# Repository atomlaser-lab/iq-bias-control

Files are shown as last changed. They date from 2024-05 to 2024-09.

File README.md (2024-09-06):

# IQ Modulator Bias Control

This project implements a digital bias controller for an IQ modulator running in carrier-suppressed single-sideband (CS-SSB) mode.  It is based on [this paper](http://opg.optica.org/ao/abstract.cfm?uri=ao-62-1-1) which detailed an analog stabilisation scheme using the same technique.  Our arXiv submission, with more detail about our digital implementation and performance, can be found [here](https://arxiv.org/abs/2408.16678).  The basic idea is to add a low frequency signal to the main, high frequency signal used for CS-SSB and use the low frequency signal to measure the phase biases in the different Mach-Zehnder interferometers (MZIs) that make up the IQ modulator.  Whereas the original work used purely analog techniques, this project levarages the fast analog input/output capabilities of the Red Pitaya STEMlab 125-14 platform.  

# Software set up

  1. Clone both this repository and the interface repository at [https://github.com/atomlaser-lab/red-pitaya-interface](https://github.com/atomlaser-lab/red-pitaya-interface) to your computer.  

  2. Connect the Red Pitaya (RP) board to an appropriate USB power source (minimum 2 A current output), and then connect it to the local network using an ethernet cable.  Using SSH (via terminal on Linux/Mac or something like PuTTY on Windows), log into the RP using the hostname `rp-{MAC}.local` where `{MAC}` is the last 6 characters of the RP's MAC address which is written on the ethernet connector.  Your network may assign its own domain, so `.local` might not be the correct choice.  The default user name and password for RPs is `root`.  Once logged in, create two directories called `iq-bias-control` and `server`.

  3. From this repository, copy over all files in the 'software/programs/' directory to the `iq-bias-control` directory on the RP using either `scp` (from a terminal on your computer) or using your favourite GUI (I recommend WinSCP for Windows).  Also copy over the file `fpga/iq-bias-control.bit` to the `iq-bias-control` directory.  From the interface repository, copy over all files ending in '.py' and the file 'get_ip.sh' to the `server` directory on the RP.

  4. On the RP and in the `iq-bias-control` directory, compile the C programs.  You can compile these using the Makefile by running the command `make` with no arguments.  This will compile all the C programs in the directory.  

  5. In the `server` directory, change the privileges of `get_ip.sh` using `chmod a+x get_ip.sh`.  Check that running `./get_ip.sh` produces a single IP address (you may need to install dos2unix using `apt install dos2unix` and then run `dos2unix get_ip.sh` to make it work).  If it doesn't, run the command `ip addr` and look for an IP address that isn't `127.0.0.1` (which is the local loopback address).  There may be more than one IP address -- you're looking for one that has tags 'global' and 'dynamic'.  Here is the output from one such device:
   ```
   root@rp-f0919a:~# ip addr
   1: lo: <LOOPBACK,UP,LOWER_UP> mtu 65536 qdisc noqueue state UNKNOWN group default qlen 1
      link/loopback 00:00:00:00:00:00 brd 00:00:00:00:00:00
      inet 127.0.0.1/8 scope host lo
         valid_lft forever preferred_lft forever
      inet6 ::1/128 scope host 
         valid_lft forever preferred_lft forever
   2: eth0: <BROADCAST,MULTICAST,UP,LOWER_UP> mtu 1500 qdisc pfifo_fast state UP group default qlen 1000
      link/ether 00:26:32:f0:91:9a brd ff:ff:ff:ff:ff:ff
      inet 169.254.176.82/16 brd 169.254.255.255 scope link eth0
         valid_lft forever preferred_lft forever
      inet 192.168.1.109/24 brd 192.168.1.255 scope global dynamic eth0
         valid_lft 77723sec preferred_lft 77723sec
   3: sit0@NONE: <NOARP> mtu 1480 qdisc noop state DOWN group default qlen 1
      link/sit 0.0.0.0 brd 0.0.0.0
   ```
   The IP address we want here is the address `192.168.1.109` as it has the `global` tag, which is what `get_ip.sh` looks for.  If you have your RP connected directly to your computer it will not work and you will have to specify the IP address manually.

   6. Upload the bitstream to the FPGA by navigating to the `iq-bias-control` directory and running `cat iq-bias-control.bit > /dev/xdevcfg`.

   7. Start the Python server by navigating to the `iq-bias-control` directory and running `python3 /root/server/appserver.py`.  If you need to specify your IP address run instead `python3 /root/server/appserver.py <ip address>`.  The script will print the IP address it is using on the command line, saying `Listening on <IP address>`.

   8. On your computer in MATLAB, add the interface repository directory to your MATLAB path.

   9. Navigate to this repository's software directory (or add it to the MATLAB path), and create a new control object using `d = IQBiasControl(<ip address>)` where `<ip address>` is the IP address of the RP.  If the FPGA has just been reconfigured, set the default values using `d.setDefaults` and upload them using `d.upload`.  If you want to retrieve the current operating values use the command `d.fetch`.

   10. You can control the device using the command line, but the recommended method is to use the GUI.  Start the GUI by running the command `IQ_Bias_Control_GUI(d)`.  This will start up the GUI.  You can also run `IQ_Bias_Control_GUI(<ip address>)` if you don't have the `IQBiasControl` object in your workspace.

# Hardware set up

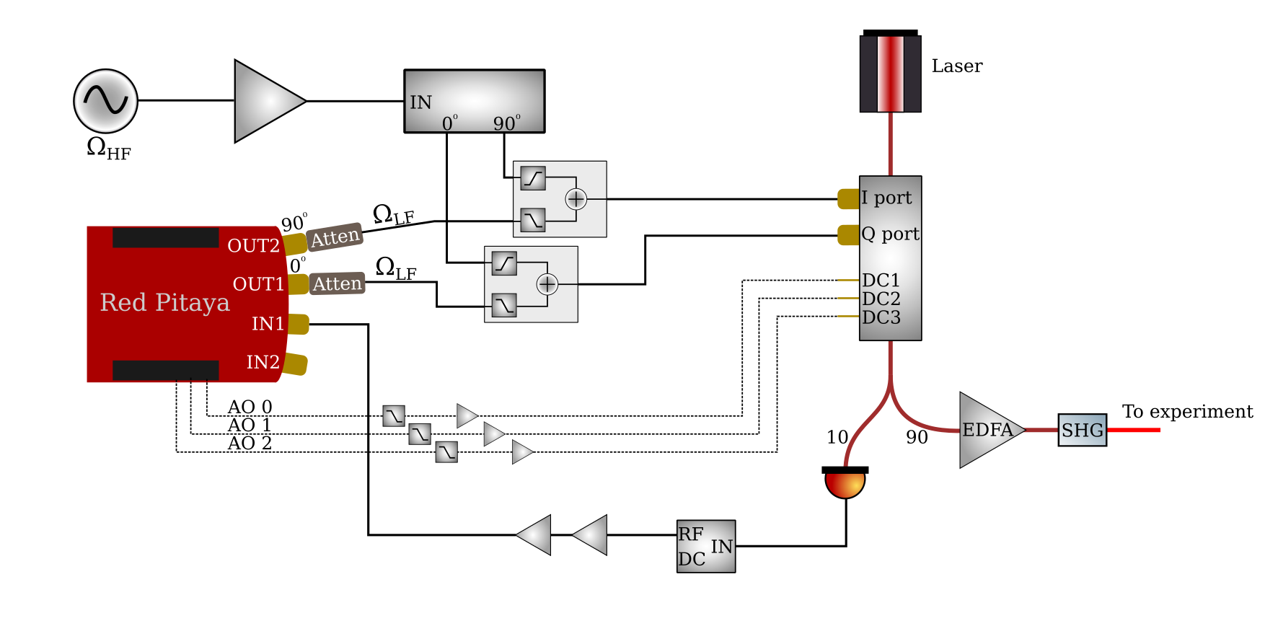
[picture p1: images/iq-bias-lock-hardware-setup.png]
Hardware setup


Connect the OUT1 and OUT2 signals to the I and Q modulation ports (order doesn't matter) on the IQ modulator.  If you want to use this with a high frequency signal as well, then you need a method of combining the low frequency signals from the Red Pitaya ($\Omega_{\rm LF}$) and the high frequency signals ($\Omega_{\rm HF}$).  The best option is to use diplexers as they have lower loss than simple power combiners.  Make sure that the output voltages/powers are within the specified tolerances of the device.  The OUT1 and OUT2 signals are already 90 degrees out of phase, so they don't need to go through a 90 degree hybrid.  You may want significant attenuation on the output ports so that the auxiliary signal is much weaker than the desired main signal.  Measure the output laser power using a photodiode of sufficient bandwidth, filter out the DC component using a high-pass filter or a bias tee, amplify as necessary, and connect to the IN1 connector.  On the LV setting the IN1 input can only measure a peak voltage of 1 V, or 10 dBm.  

Connect the slow analog outputs 0-2 to the IQ modulator's DC biases: see [this page](https://redpitaya.readthedocs.io/en/latest/developerGuide/hardware/125-14/extent.html) for the pinout.  You may need to amplify these signals (maximum output is 1.6 V) to get the right voltage range.  The slow analog outputs are pulse width modulation (PWM) outputs with a 250 MHz clock and 10 bits of resolution, so the PWM frequency is about 244 kHz.  You will likely want additional filtering on the outputs for driving the DC biases.  Take care if you use aluminium electrolytic capacitors for the filter, as the equivalent series resistance (ESR) can severely compromise filtering capabilities at high frequencies.  

Alternatively, you can build the included "shield" for the Red Pitaya that connects to the PWM analog outputs, filters them, and amplifies them to be in the range [0,14.6] V. The corner frequency is approximately 200 Hz, which suppresses the power at the fundamental PWM frequency of 244 kHz by about 57 dB.  Choosing different filtering capacitors will give you different suppression and bandwidths.  A KiCAD project is provided in the `board-design/` directory in addition to Gerber files in `board-design/generated/` for manufacturing.  We have had good experiences with JLCPCB in manufacturing boards.  Part lists `red-pitaya-pwm-shield.txt` and `additional-parts.txt` provide Digikey part numbers for components.

Digital inputs DIO0_N and DIO1_N provide additional control over feedback (see [this page](https://redpitaya.readthedocs.io/en/latest/developerGuide/hardware/125-14/extent.html)).  DIO0_N is a digital input that controls the sample-and-hold system and is OR'ed with the software sample-and-hold setting.  When high (3.3 V logic), it enables sample-and-hold.  DIO1_N is a digital input that can be used to turn off the RF output from the RP; when high (3.3 V logic), it turns off the RF output.

# Using the GUI

The GUI is best way to control the device.  There are four categories of device settings plus the application settings.

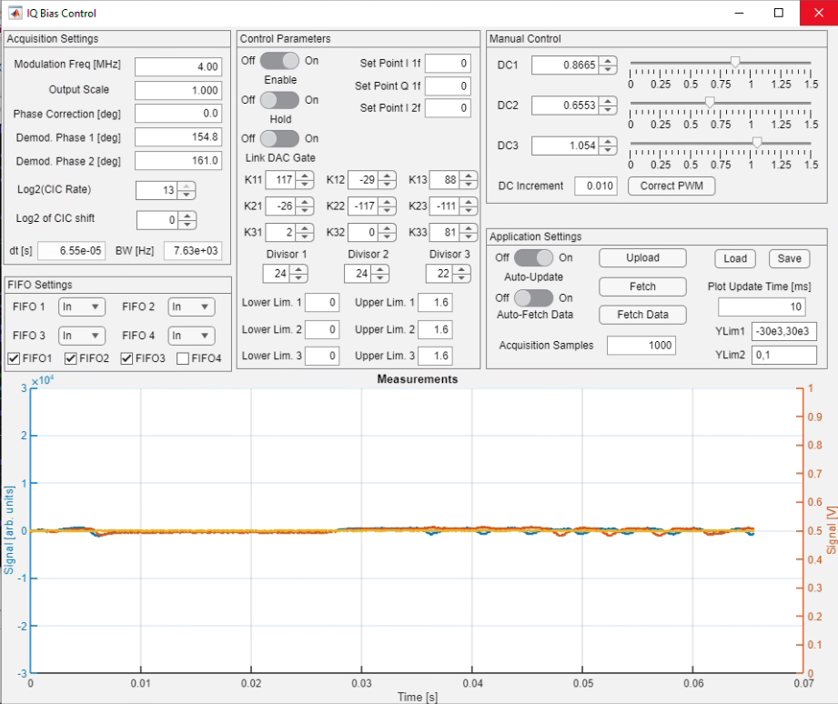
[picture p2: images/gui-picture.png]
Example GUI


## Acquisition Settings

The idea behind this technique is to generate a low-frequency modulation signal at a few MHz, inject it into the IQ modulator, measure the laser power using a photodetector, and then demodulate that signal at the modulation frequency in both quadratures (in-phase I and quadrature-phase Q), and also to demodulate at twice the modulation frequency (both I and Q are provided).  Demodulation is implemented digitally by multiplying the input signal with a sinusoidally varying signal at the correct frequency but with a demodulation phase (1 and 2), and the result is then filtered using a CIC filter with a rate of $2^N$.  So under acquisition settings, "Modulation Freq" is the modulation frequency output from the RP, "Demod Phase 1" and "Demod Phase 2" are the demodulation phases at the modulation frequency and its second harmonic, "Log2(CIC Rate)" is $N$, and "Log2 of CIC shift" is an additional digital scaling factor that amplifies/attenuates the output signals by $2^M$ where $M$ is the integer given in the control.  The time step between filtered samples, and the equivalent bandwidth, is given at the bottom of the panel.

## Control

Assuming that the demodulation phases are properly set, the bias voltages on the IQ modulator should independently control each demodulated signal with very limited cross-coupling.  In reality, there can be significant cross-coupling.  To account for cross-coupling, we use a multi-dimensional integral control scheme.  For a vector of output voltages $\mathbf{v}$, a vector of signals $\mathbf{s}$, and a vector of set-points $\mathbf{r}$, we implement a control law as a 3x3 matrix $K$ such that $\mathbf{v} = K\int(\mathbf{r} - \mathbf{s})dt$.  The integer values for the control matrix $K$ are given as K11, K12, etc, and these can be negative to allow for opposite polarity responses.  Additionally, to account for possibly different orders of magnitude of gain reponse, each output voltage has its own "divisor" to allow for fixed-point arithmetic.  Therefore, the output voltage $v_1$ is $v_1 = 2^{-N_1}(K_{11}s_1 + K_{12}s_2 + K_{13}s_3)$, where $N_1$ is labelled as "Divisor 1", and similarly for the other rows 2 and 3.  

Other controls are reasonably straightforward.  The `Enable` switch turns the controller on, and the `Hold` switch holds the outputs at the current values.  The switch `Disable output on hold?` turns off the output DAC when the hold is enabled.  If it is set to `On`, then when the hold is engaged (either from software or from the digital input) it switches off the output DAC.  This can be used if the presence of the $\Omega_{\rm LF}$ signal is detrimental to the experiment during a pulse sequence.  

The different set points allow for stabilising the signals about a non-zero value, and the upper and lower limits at the bottom limit the PMW output voltages (values are prior to any amplifiers you may add).

## Manual Control

The voltage biases DC1, DC2, and DC3 adjust the phases of the three MZIs in the IQ modulator and thus allow for CS-SSB as well as all sorts of other, undesired output modes.  Unfortunately, simply by measuring the optical power it is fundamentally impossible to determine what frequency is on the output of the IQ modulator, as all single-frequency operation generates a steady DC value on the photodiode.  The manual control allows the user to get close to CS-SSB operation, and then the controller will ideally keep it in that mode.

DC1, DC2, and DC3 are output voltages from 0 to 1.6 V that should be connected to the appropriate pins on the IQ modulator.  These values can be changed using the sliders or spinners.  If using the arrows on the spinners, the DC increment can be changed to allow for coarser or finer changes.  Note that the minimum DC increment is 1.6 mV.

The `Correct PWM` button can be used to adjust the manual PWM values so that they are equal to the mean PWM values achieved by feedback.  When feedback is enabled, clicking `Correct PWM` will record 100 ms of the output PWM values and then it will adjust the manual values to match the mean values.

## FIFO Settings

The measurements are recorded in first-in, first-out (FIFO) buffers on chip, and then that data can be retrieved and displayed.  What data gets recorded can be changed by the user using the `FIFO 1`, `FIFO 2`, etc drop-down menus.  If they are set to `In`, the measurements after demodulation and filtering are recorded, and if they are set to `Out` the PWM values are recorded.  `In` values are plotted on the left Y axis, and `Out` values are plotted on the right Y axis.  The checkboxes control what values are plotted on the graph.

## Application Settings

`Upload` uploads all displayed settings to the RP.  `Fetch` grabs the values off of the RP and updates the display.  `Fetch Data` grabs `Acquisition Samples` number of samples after demodulation and displays that on the plot.  Change the display limits using `YLim1` for the left-hand axis and `YLim2` for the right-hand axis.  

`Auto-Update` uploads the device configuration anytime a parameter is changed.

`Auto-Fetch Data` continuously uploads parameters and fetches demodulated data and displays it on the plot.  The update time is given in `Plot Update Time` in milliseconds.  You can change the parameters as it grabs data in order to optimise the bias values.

You can also save and load bias control configurations using the `Load` and `Save` buttons.

# How to determine gain parameters

The best way to get the right gain parameters is to measure the response of the system to a change in the bias voltage, and then to calculate the gain parameters from that.  There is a script called `automatically_set_feedback.m` in the `software/` folder which does this task.  You may need to alter the script to suit your IQ modulator and system.  You will also need the MATLAB Statistics toolbox and the Optimization toolbox for the functions `range` and `fsolve`, respectively.  It is recommended that you step through the script one section at a time, checking the results as you go.  Here is how the script works.

**FEEDBACK MUST BE DISABLED TO RUN THIS SCRIPT**

You will need a rough idea of what the right bias voltages are, first.  The best way to do this is to use a scanning optical cavity, but beating the output field from the IQ modulator with a reference at a different frequency can also be used.  Adjust the manual voltages until you are close to CS-SSB operation.  Roughly, the algorithm is to iteratively adjust DC1 and DC2 to minimize the amount of power in the carrier, and then to adjust DC3 to choose the positive or negative sideband as desired.  

Once you are close, set the desired modulation frequency (multiples of 5 MHz appear to be problematic), the sample rate, and any scalings.  The first step is to measure the 2f demodulation phase.  This is done by varying the DC3 voltage and the 2f demodulation phase, and then looking at what demodulation phase gives the largest amplitude change to the 2f demodulated signal: this is the optimum demodulation phase.

The next step is to do a fine scan over the DC3 bias at the optimum demodulation phase to find the biases at which the 2f signal amplitude crosses zero.  There are two voltages, and for the ixBlue IQ modulator that we use the voltage that corresponds to the positive sideband is the higher voltage near 0.9 V.  This gets a fine-tuned measurement.

Next, we perform a scan over the DC2 bias and the 1f demodulation phase to determine the optimal phase.  Again, we look at what phase gives the maximum amplitude change to the 1f Q signal.  By definition, this minimizes cross-coupling with the 1f I signal.

With the correct 1f demodulation phase, a fine scan is applied to determine the voltages at which the 1f I and Q signals cross zero.  There will likely be two zero crossings for each of the I and Q signals, so you will need to use additional information, such as an optical cavity, to determine which ones correspond to CS-SSB mode.

We then do two steps of small variations about the bias voltages that we have measured to give zero signal.  We then fit the measurements to a linear response to get a transfer matrix $G$ (the slope of the lines) and new zero crossing voltages $\mathbf{z}$.  We then re-measure the responses around these new zero-crossing voltages, which gives a final transfer matrix $G$.  You should check that the plots of this transfer matrix show the measured signals going through zero when the DC voltages are at their nominal values.

We then measure the dynamic response by applying a step change to the DC voltages and measuring the time-dependent relaxation of the measured signals.  

The feedback matrix is then calculated by starting with a target matrix $K_t$ and computing $K = G^{-1}K_t$.  For critical damping, the elements of $K_t$ should be $[K_t]_{ii} = [\Gamma]^{1/2}_{ii}/2$.

# Troubleshooting

## CS-SSB operation lost

If your scanning optical cavity is showing that CS-SSB operation has been lost, then it is highly likely that the bias lock has been lost.  This can occur if the locking system has been kicked out of its capture range by, for instance, a large temperature change.  Alternatively, charge can accumulate on the electrodes and in the LiNBO3 that affects the optimum bias voltages.  Similarly, charge can be freed by the optical field that then affects the response.

  1. DISABLE THE LOCK.  If you leave the lock on while changing the biases, it will do very weird things.
  2. If, after disabling the lock, the system returns to near CS-SSB operation, try re-engaging the lock.
  3. If this doesn't work, disable the lock, manually re-optimise the biases, re-optimise the lock parameters, and then re-lock.

## GUI unresponsive

If the GUI appears unresponsive, in that changing GUI parameters such as biases or the lock enable status appears to do nothing:

  1. IS THE LOCK ENGAGED?  If the lock is engaged and you try to change the bias voltages, it might appear that nothing is happening because the lock forces the system into CS-SSB operation.
  2. IS AUTO_UPDATE DISABLED?  If Auto-Update is disabled, then changed parameters on the GUI will not be uploaded to the device.  Set Auto-Update to "On".
  3. Has the Red Pitaya been disconnected from the network?  Bring up the PuTTY or terminal window that is logged into the Red Pitaya.  If the server is running, use CTRL-Z to suspend it.  If the terminal throws an error, like "Connection lost" or somesuch, then reconnect to the Red Pitaya (on PuTTY you can right-click on the window's title bar and click "Reconnect").  Navigate back to the `iq-bias-control` directory using `cd iq-bias-control` and start the Python server again using `python3 /root/server/appserver.py`.  If the running server suspended without error, bring it back to the foreground using the command `fg`.
  4. Is the figure data in the GUI not updating?  This is probably just an error in the timer used for non-command-line-blocking fetching of the data.  Set Auto-Fetch Data to "Off" and then "On" again.

# Creating the project

When creating the project, use Vivado 2023.2.

To create the project, clone the repository to a directory on your computer, open Vivado, navigate to the fpga/ directory (use `pwd` in the TCL console to determine your current directory and `cd` to navigate, just like in Bash), and then run `source make-project.tcl` which will create the project files under the directory `basic-project`.  If you want a different file name, open the `make-project.tcl` file and edit the line under the comment `# Set the project name`.  This should create the project with no errors.  It may not correctly assign the AXI addresses, so you will need to open the address editor and assign the `PS7/AXI_Parse_0/s_axi` interface the address range `0x4000_000` to `0x7fff_ffff`.

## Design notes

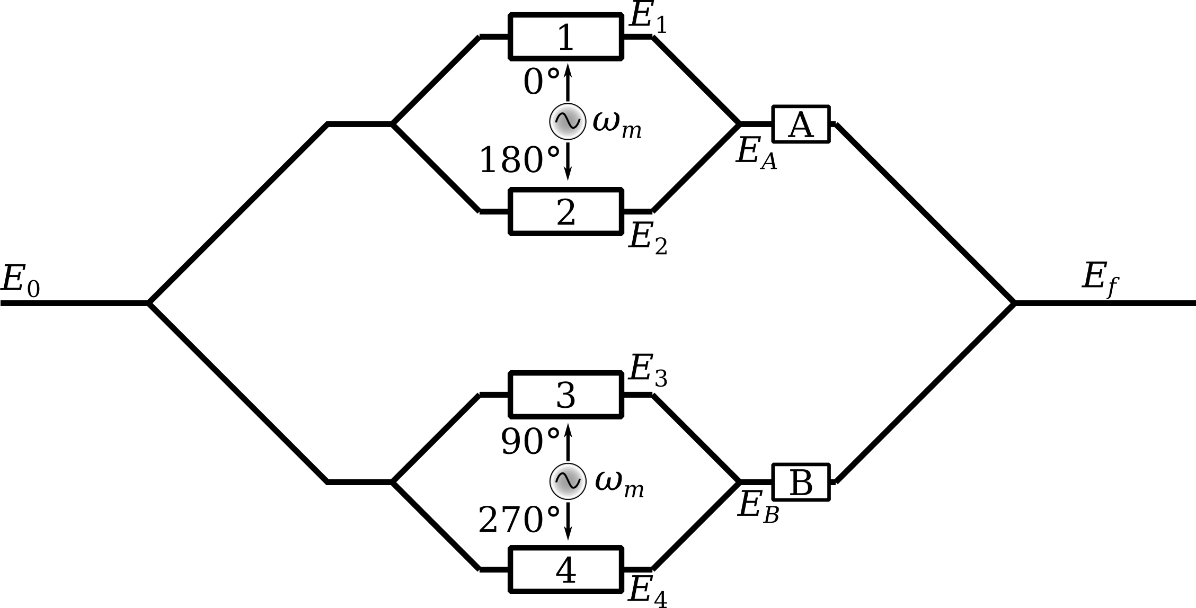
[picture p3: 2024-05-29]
images/iq-modulator-diagram.png

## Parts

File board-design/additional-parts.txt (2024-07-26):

"Part number", "Quantity", "Description"
"1276-1106-1-ND", "12", "0.22u cap"
"1276-1264-1-ND", "12", "2.2u cap"
"1276-1097-1-ND", "12", "1u cap",
"399-C1206C104K5RAC7800CT-ND", "12", "0.1u cap"

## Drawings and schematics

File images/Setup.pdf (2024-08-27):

(a)

3

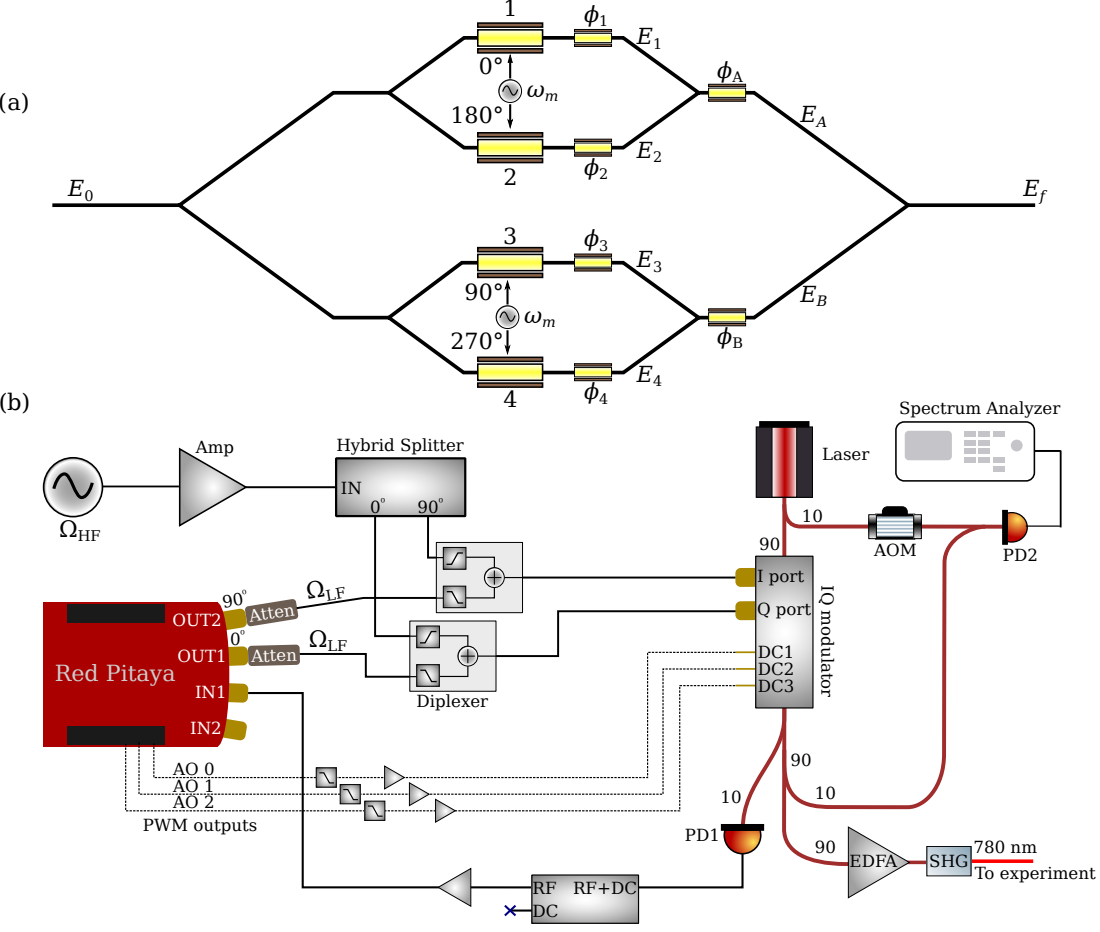
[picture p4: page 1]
OUT2; OUT1; Red Pitaya; Atten; Laser Amp; Hybrid Splitter; PWM outputs; Spectrum Analyzer; I port; IQ modulator; Q port; SHG; AOM; ΩHF; ΩLF; To experiment; Diplexer; EDFA; RF+DCRF DC

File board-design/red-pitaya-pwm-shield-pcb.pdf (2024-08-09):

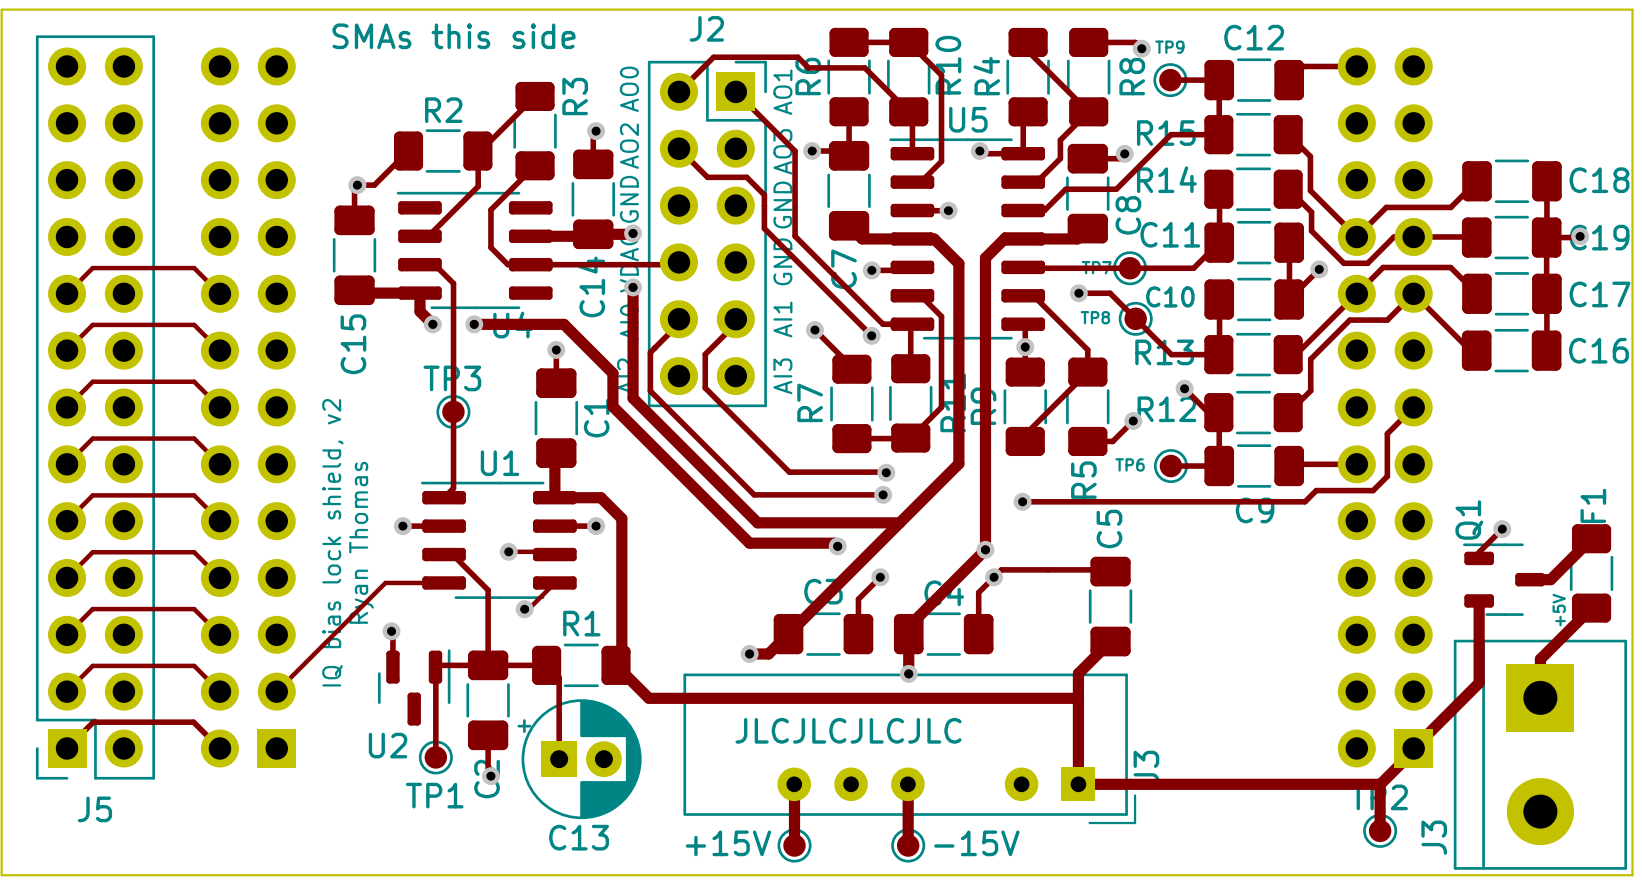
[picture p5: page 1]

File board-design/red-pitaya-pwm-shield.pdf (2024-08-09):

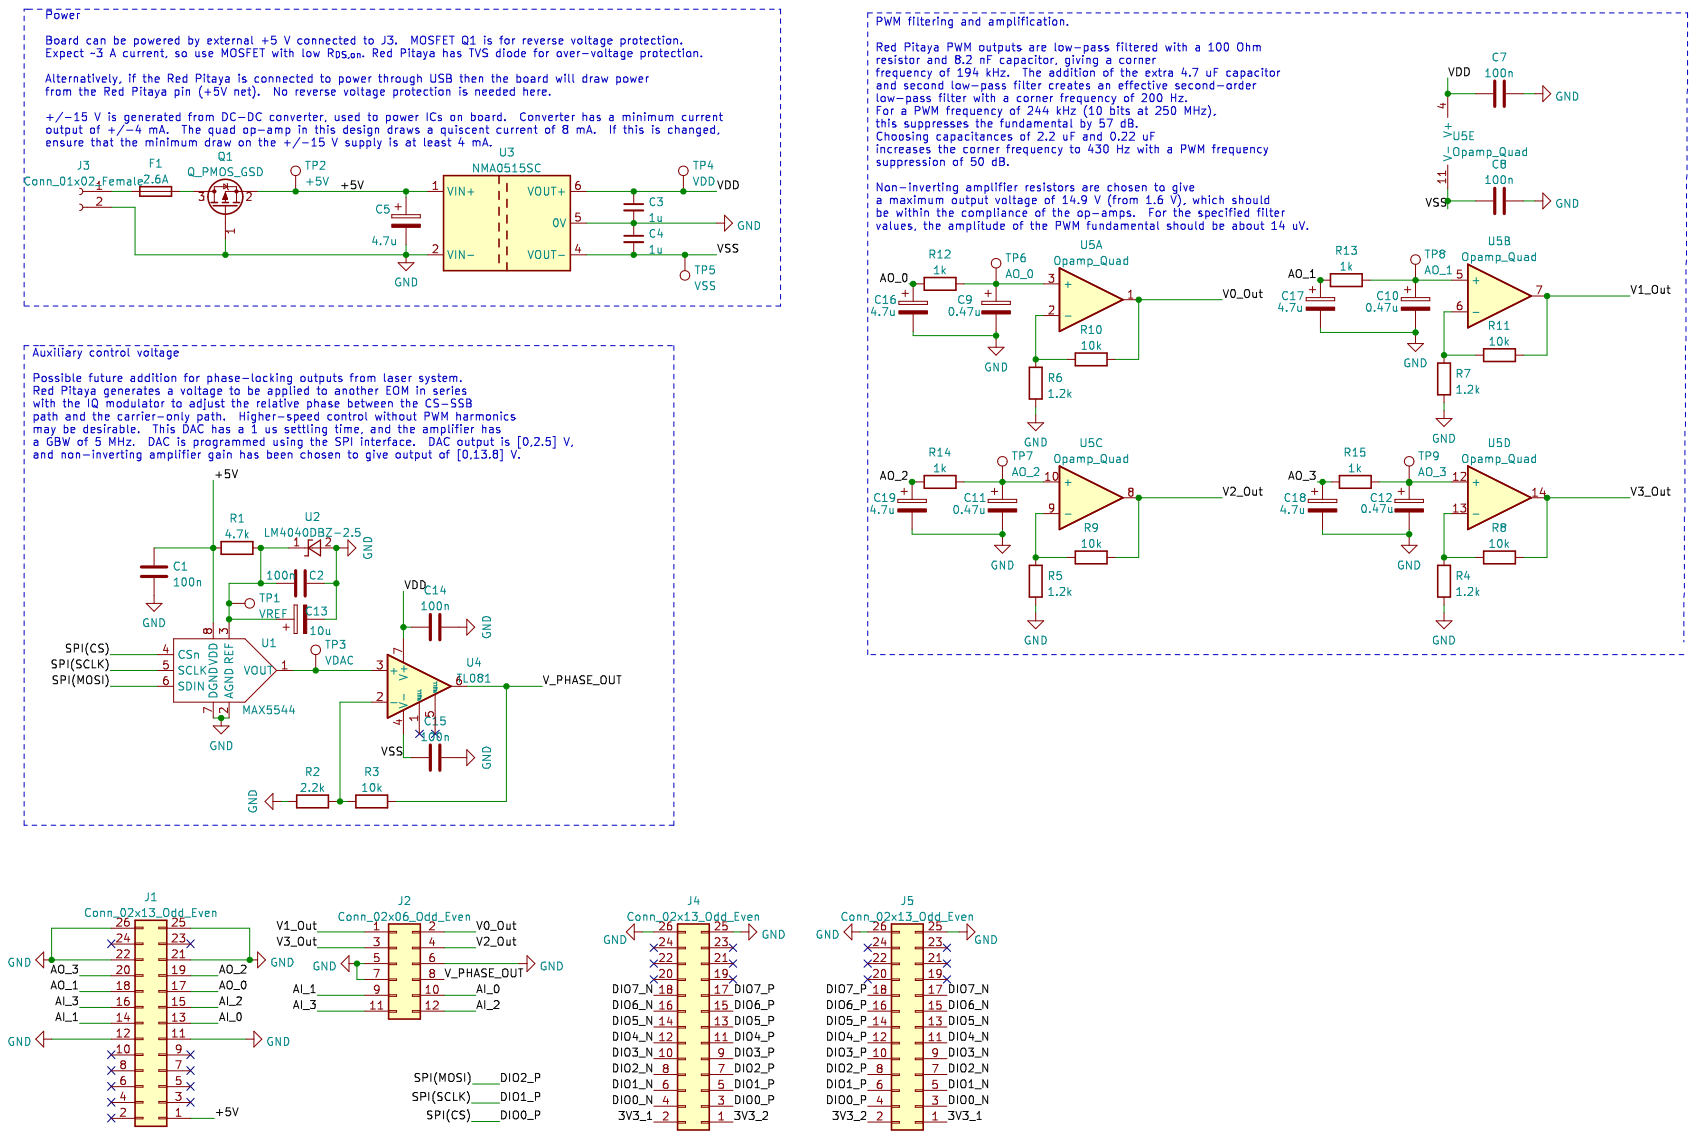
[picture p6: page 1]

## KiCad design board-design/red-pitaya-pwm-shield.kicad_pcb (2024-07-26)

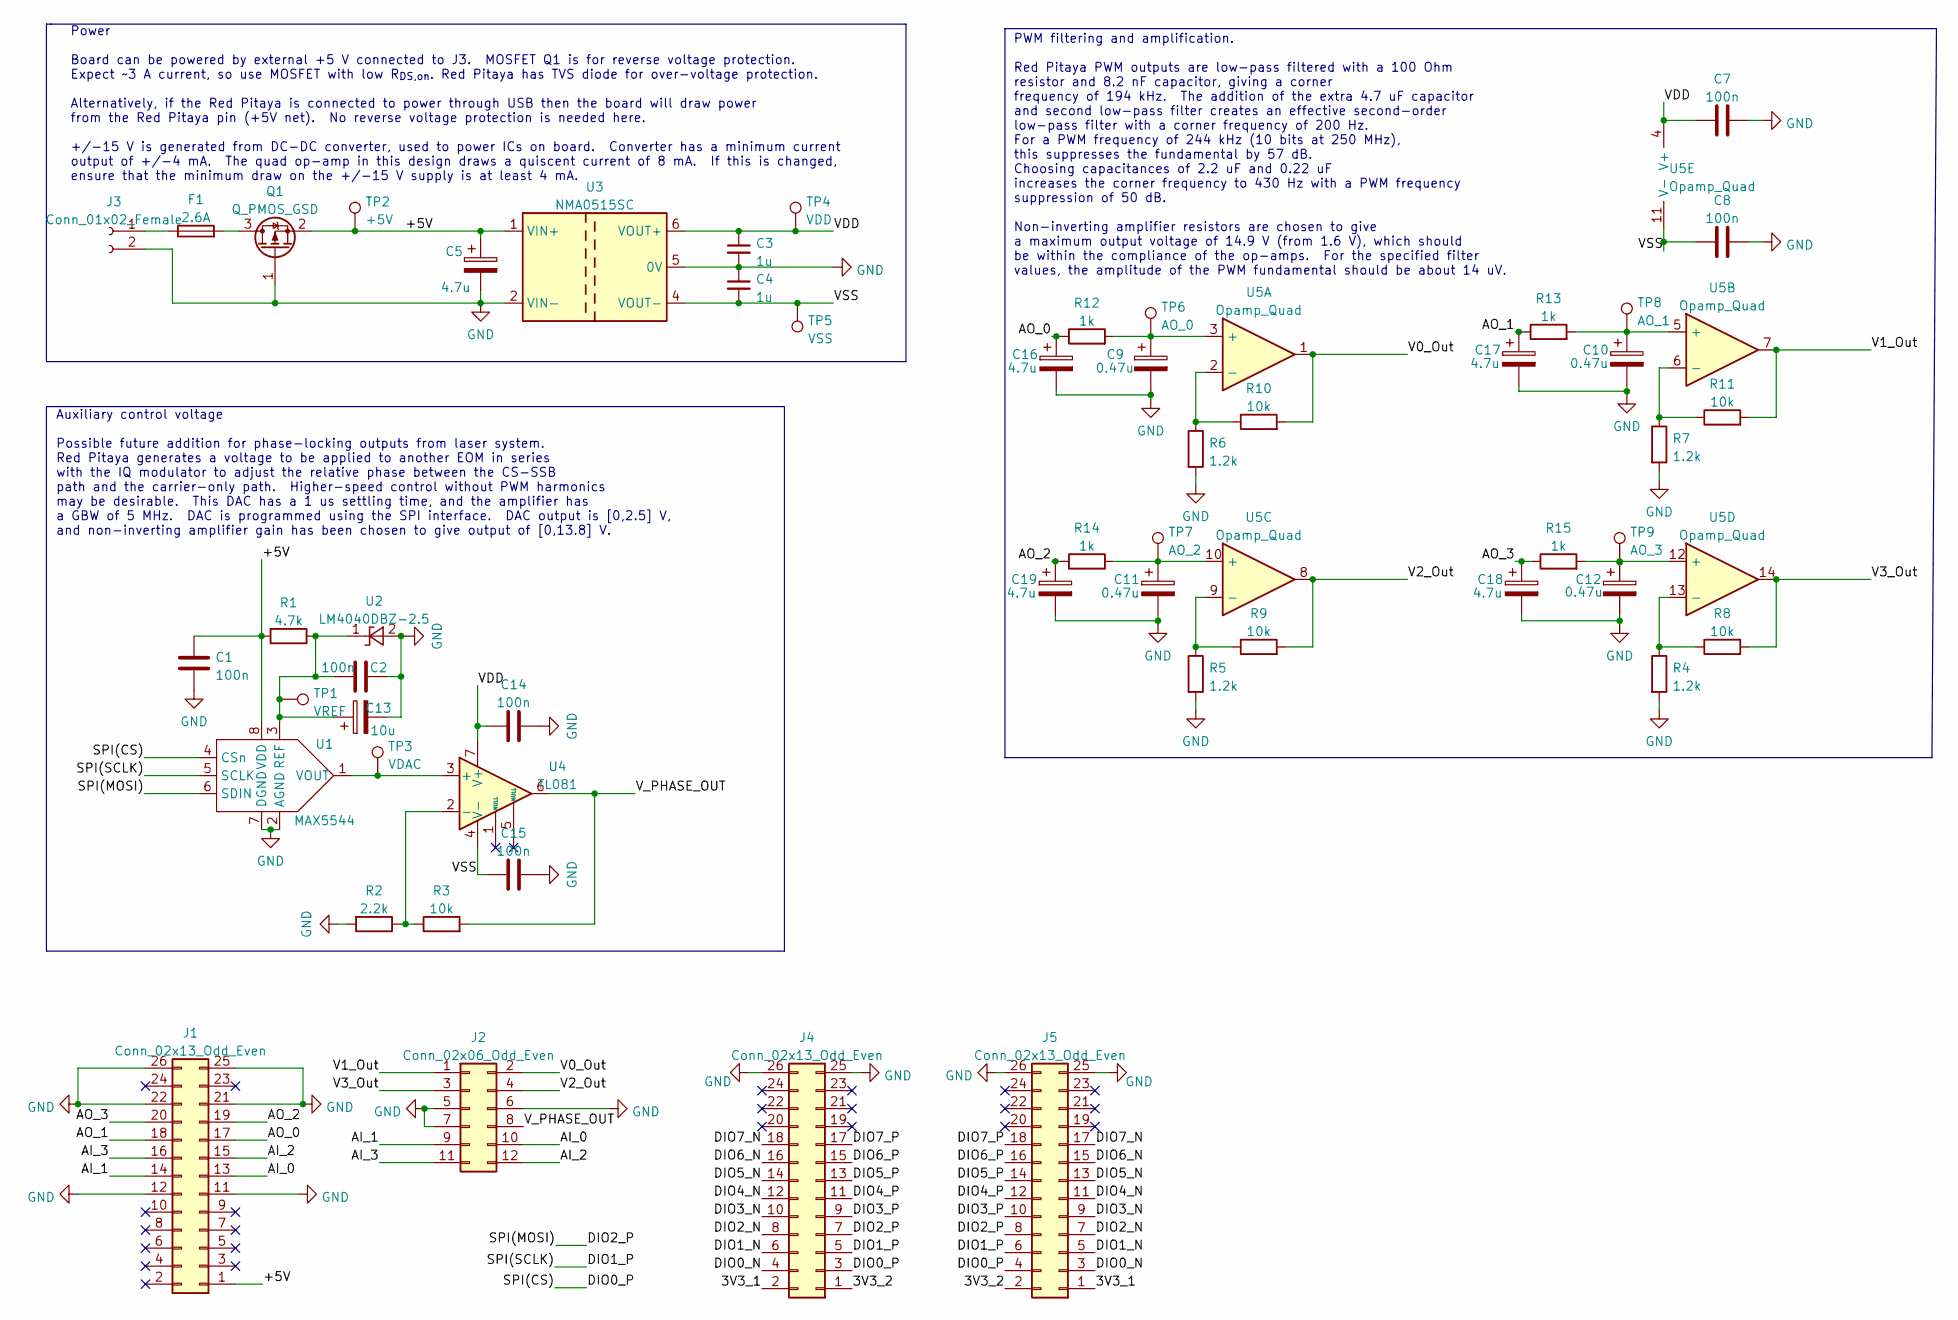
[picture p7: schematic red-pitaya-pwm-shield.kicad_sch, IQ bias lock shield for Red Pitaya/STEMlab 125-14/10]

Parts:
C1, C2, C7, C8, C14, C15: 100n; C_1206_3216Metric_Pad1.33x1.80mm_HandSolder; Digikey Part Number 399-C1206C104K5RAC7800CT-ND
C3, C4: 1u; C_1206_3216Metric_Pad1.33x1.80mm_HandSolder; Digikey Part Number 1276-1097-1-ND
C5, C16, C17, C18, C19: 4.7u; C_1206_3216Metric_Pad1.33x1.80mm_HandSolder; Digikey Part Number 1276-3179-1-ND
C9, C10, C11, C12: 0.47u; C_1206_3216Metric_Pad1.33x1.80mm_HandSolder; Digikey Part Number 1276-1118-1-ND
C13: 10u; CP_Radial_D5.0mm_P2.00mm; Digikey Part Number 732-8937-1-ND
F1: 2.6A; R_1206_3216Metric_Pad1.30x1.75mm_HandSolder; Digikey Part Number 2315-SBF32252ASTPCT-ND
J1, J4: Conn_02x13_Odd_Even; PinSocket_2x13_P2.54mm_Vertical; Digikey Part Number SAM11136-ND
J2: Conn_02x06_Odd_Even; PinSocket_2x06_P2.54mm_Vertical; Digikey Part Number 732-61300621821-ND
J3: Conn_01x02_Female; TerminalBlock_bornier-2_P5.08mm; Digikey Part Number 732-10955-ND
J5: Conn_02x13_Odd_Even; PinSocket_2x13_P2.54mm_Vertical; Digikey Part Number 732-61302621821-ND
Q1: Q_PMOS_GSD; SOT-23-3; Digikey Part Number DMP3099L-7DICT-ND
R1: 4.7k; R_1206_3216Metric_Pad1.30x1.75mm_HandSolder; Digikey Part Number 311-4.70KFRCT-ND
R2: 2.2k; R_1206_3216Metric_Pad1.30x1.75mm_HandSolder; Digikey Part Number RMCF1206JT2K20CT-ND
R3, R8, R9, R10, R11: 10k; R_1206_3216Metric_Pad1.30x1.75mm_HandSolder; Digikey Part Number 1292-WR12X103JTLCT-ND
R4, R5, R6, R7: 1.2k; R_1206_3216Metric_Pad1.30x1.75mm_HandSolder; Digikey Part Number RMCF1206JT1K20CT-ND
R12, R13, R14, R15: 1k; R_1206_3216Metric_Pad1.30x1.75mm_HandSolder; Digikey Part Number RMCF1206JT1K00CT-ND
TP1: VREF; TestPoint_Pad_D1.0mm
TP2: +5V; TestPoint_Pad_D1.0mm
TP3: VDAC; TestPoint_Pad_D1.0mm
TP4: VDD; TestPoint_Pad_D1.0mm
TP5: VSS; TestPoint_Pad_D1.0mm
TP6: AO_0; TestPoint_Pad_D1.0mm
TP7: AO_2; TestPoint_Pad_D1.0mm
TP8: AO_1; TestPoint_Pad_D1.0mm
TP9: AO_3; TestPoint_Pad_D1.0mm
U1: MAX5544; SOIC-8_3.9x4.9mm_P1.27mm; Digikey Part Number MAX5544CSA+-ND
U2: LM4040DBZ-2.5; SOT-23; Digikey Part Number 576-1047-1-ND
U3: NMA0515SC; Converter_DCDC_Murata_NMAxxxxSC_THT; Digikey Part Number 811-1453-5-ND
U4: TL081; SOIC-8_3.9x4.9mm_P1.27mm; Digikey Part Number 296-TL081HIDRCT-ND
U5: Opamp_Quad; SOIC-14_3.9x8.7mm_P1.27mm; Digikey Part Number MC33079DR2GOSCT-ND

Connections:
/3V3_1: J4.2, J5.1
/3V3_2: J4.1, J5.2
/+5V: C1.2, C5.1, J1.1, Q1.2 (S), R1.2, TP2.1, U1.8 (VDD), U3.1 (VIN+)
/AI_0: J1.13, J2.10
/AI_1: J1.14, J2.9
/AI_2: J1.15, J2.12
/AI_3: J1.16, J2.11
/AO_0: C16.1, J1.17, R12.1
/AO_1: C17.1, J1.18, R13.1
/AO_2: C19.1, J1.19, R14.1
/AO_3: C18.1, J1.20, R15.1
/DIO0_N: J4.4, J5.3
/DIO0_P: J4.3, J5.4, U1.4 (CSn)
/DIO1_N: J4.6, J5.5
/DIO1_P: J4.5, J5.6, U1.5 (SCLK)
/DIO2_N: J4.8, J5.7
/DIO2_P: J4.7, J5.8, U1.6 (SDIN)
/DIO3_N: J4.10, J5.9
/DIO3_P: J4.9, J5.10
/DIO4_N: J4.12, J5.11
/DIO4_P: J4.11, J5.12
/DIO5_N: J4.14, J5.13
/DIO5_P: J4.13, J5.14
/DIO6_N: J4.16, J5.15
/DIO6_P: J4.15, J5.16
/DIO7_N: J4.18, J5.17
/DIO7_P: J4.17, J5.18
/V0_Out: J2.2, R10.2, U5.1
/V1_Out: J2.1, R11.2, U5.7
/V2_Out: J2.4, R9.2, U5.8
/V3_Out: J2.3, R8.2, U5.14
/VDD: C3.1, C7.1, C14.2, TP4.1, U3.6 (VOUT+), U4.7 (V+), U5.4 (V+)
/VSS: C4.2, C8.1, C15.2, TP5.1, U3.4 (VOUT-), U4.4 (V-), U5.11 (V-)
/V_PHASE_OUT: J2.8, R3.2, U4.6
GND: C1.1, C2.2, C3.2, C4.1, C5.2, C7.2, C8.2, C9.2, C10.2, C11.2, C12.2, C13.2, C14.1, C15.1, C16.2, C17.2, C18.2, C19.2, J1.11, J1.12, J1.21, J1.22, J1.25, J1.26, J2.5, J2.6, J2.7, J3.2, J4.25, J4.26, J5.25, J5.26, Q1.1 (G), R2.2, R4.2, R5.2, R6.2, R7.2, U1.2 (AGND), U1.7 (DGND), U2.2 (A), U3.2 (VIN-), U3.5 (0V)
unnamed: C9.1, R12.2, TP6.1, U5.3 (+)
unnamed: C10.1, R13.2, TP8.1, U5.5 (+)
unnamed: C11.1, R14.2, TP7.1, U5.10 (+)
unnamed: C12.1, R15.2, TP9.1, U5.12 (+)
unnamed: C2.1, C13.1, R1.1, TP1.1, U1.3 (REF), U2.1 (K)
unnamed: F1.1, J3.1
unnamed: F1.2, Q1.3 (D)
unnamed: R2.1, R3.1, U4.2 (-)
unnamed: R4.1, R8.1, U5.13 (-)
unnamed: R5.1, R9.1, U5.9 (-)
unnamed: R6.1, R10.1, U5.2 (-)
unnamed: R7.1, R11.1, U5.6 (-)
unnamed: TP3.1, U1.1 (VOUT), U4.3 (+)

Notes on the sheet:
Auxiliary control voltage Possible future addition for phase-locking outputs from laser system. Red Pitaya generates a voltage to be applied to another EOM in series with the IQ modulator to adjust the relative phase between the CS-SSB path and the carrier-only path. Higher-speed control without PW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
PWM filtering and amplification. Red Pitaya PWM outputs are low-pass filtered with a 100 Ohm resistor and 8.2 nF capacitor, giving a corner frequency of 194 kHz. The addition of the extra 4.7 uF capacitor and second low-pass filter creates an effective second-order low-pass filter with a corner fre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
Power Board can be powered by external +5 V connected to J3. MOSFET Q1 is for reverse voltage protection. Expect ~3 A current, so use MOSFET with low R_{DS,on}. Red Pitaya has TVS diode for over-voltage protection. Alternatively, if the Red Pitaya is connected to power through USB then the board wi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

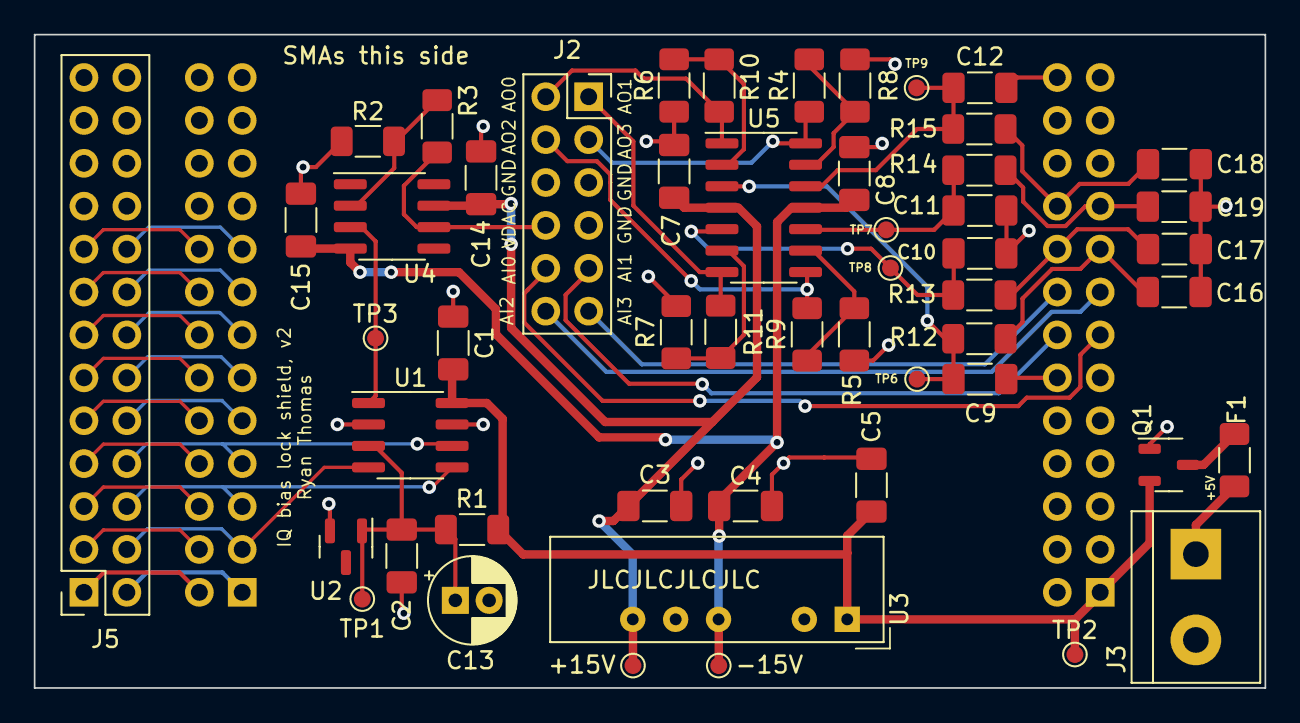
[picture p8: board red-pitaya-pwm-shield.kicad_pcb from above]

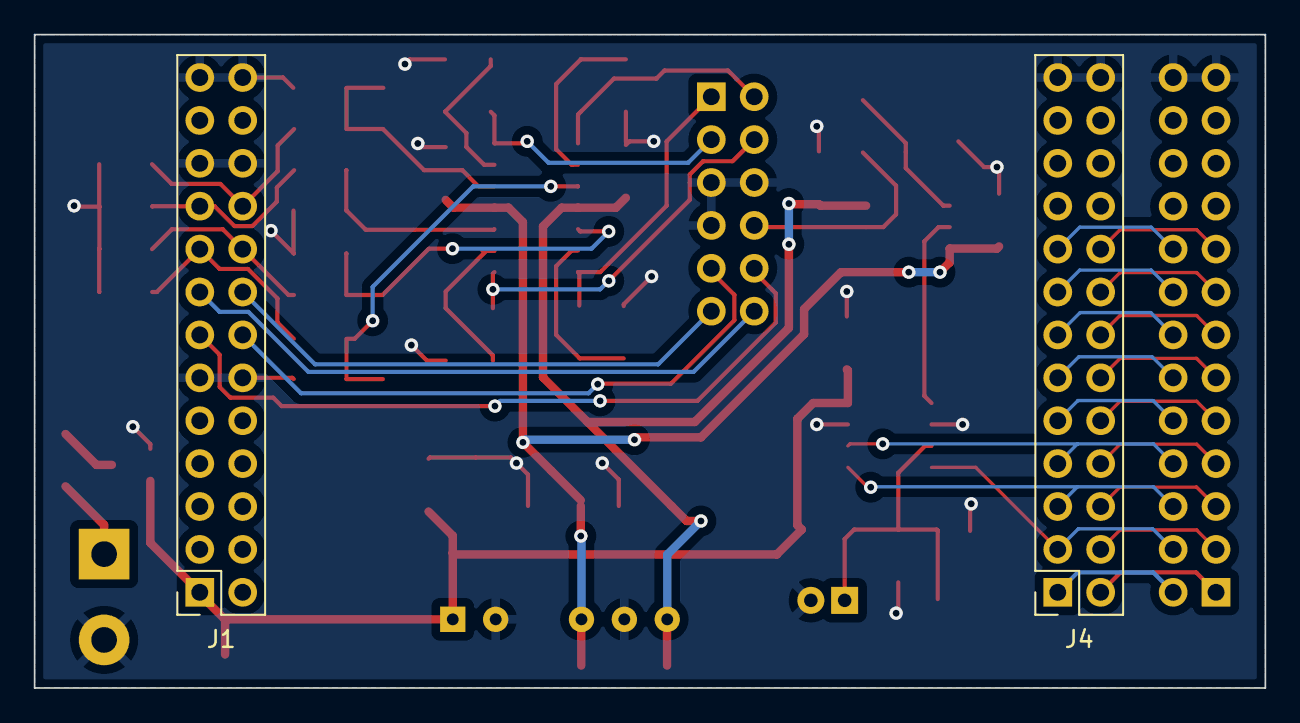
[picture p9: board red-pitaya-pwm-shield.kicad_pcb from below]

Board: 2 copper layers, 72.9 x 38.7 mm, 54 parts (2 on the bottom side), 48 nets.

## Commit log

2023-11-08 Modified DeviceControl, removed other classes
2023-11-09 Increased filter output width
2023-11-14 Minor bug fix to DeviceControl. Memory reading works
2023-12-21 Added max voltage for C voltage scan function
2023-12-22 Updated DeviceControl to upload/fetch using a single TCP transaction
    Also added an auto_retry function
2024-01-10 Added PID stuff to GUI. Doesn't currently work
2024-01-29 Changed GUI for coupled control. Untested on device
2024-01-31 Added Demodulator_tb file, updated topmod_tb. Minor change to feedback calc.
    Vivado won't simulate Demodulator.vhd as is because it has some
    undefined issue with the shift_right operation at the very end
    of the CIC filters. Fixing the value to a constant solves the
    problem, though.
2024-05-03 Added PCB design with bipolar DAC.
    [red-pitaya-pwm-shield.kicad_pcb, red-pitaya-pwm-shield.kicad_sch]
2024-05-03 Mostly routed board design
    [red-pitaya-pwm-shield.kicad_pcb, red-pitaya-pwm-shield.kicad_sch]
2024-05-03 Switched to unipolar DAC, routed board, assigned parts. Generated BOM
    [red-pitaya-pwm-shield.kicad_pcb, red-pitaya-pwm-shield.kicad_sch]
2024-05-03 Added generated PDFs
    [red-pitaya-pwm-shield.kicad_pcb]
2024-05-06 Updated text on schematic, fixed position of headers on PCB
    [red-pitaya-pwm-shield.kicad_pcb, red-pitaya-pwm-shield.kicad_sch]
2024-05-07 Added fuse, removed Zener diode. Added test points. Generated Gerber files
    [red-pitaya-pwm-shield-B_Cu.gbr, red-pitaya-pwm-shield-B_Mask.gbr, red-pitaya-pwm-shield-B_Paste.gbr, red-pitaya-pwm-shield-B_Silkscreen.gbr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]
2024-05-07 Added silkscreen text for order number placement
    [red-pitaya-pwm-shield-B_Cu.gbr, red-pitaya-pwm-shield-B_Mask.gbr, red-pitaya-pwm-shield-B_Paste.gbr, red-pitaya-pwm-shield-B_Silkscreen.gbr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]
2024-05-09 Fixed bug in measuring linear responses. PWM voltages were not reset to zero
2024-05-20 Minor changes for new board
2024-05-31 Added function to auto script to look for zero closest to current values
2024-06-05 Added some matlab simulation files for PWM filtering
2024-06-11 Updated board design with better low-pass filter
    [red-pitaya-pwm-shield.kicad_pcb, red-pitaya-pwm-shield.kicad_sch]
2024-07-26 Eliminated use of PS SPI, changed board.
    SPI accessed through PS is not able to be used in programmable
    logic since the ports are not accessible. Switched to using
    3 pins from the E1 connector. Changed PCB to match.
    [red-pitaya-pwm-shield-B_Cu.gbr, red-pitaya-pwm-shield-B_Mask.gbr, red-pitaya-pwm-shield-B_Paste.gbr, red-pitaya-pwm-shield-B_Silkscreen.gbr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]
2024-08-08 Changed PID module with divisors for each gain coefficient
    Also expanded size of measurements to try and avoid integer overflow
    Also added ability to lock to Q measurement rather than phase in
    case of low SNR.
2024-08-27 Renamed DeviceControl object, added comments, improved README
2024-10-28 Updated board design
